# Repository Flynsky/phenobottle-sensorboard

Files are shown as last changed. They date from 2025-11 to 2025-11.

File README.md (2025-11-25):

# Phenobottle Sensorboard
Schematic
## Getting Startet
- Connect via USB or USART0 to access a internal console.
  A good, easy to use Tool for this is the Arduino IDE. 
- Send "?" to this console for help on the avaliable commands.

## Picture
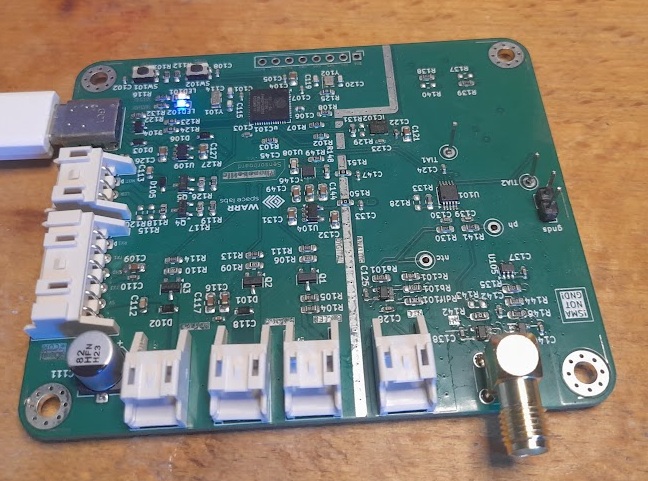
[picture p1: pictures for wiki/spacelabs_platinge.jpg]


## Hardware
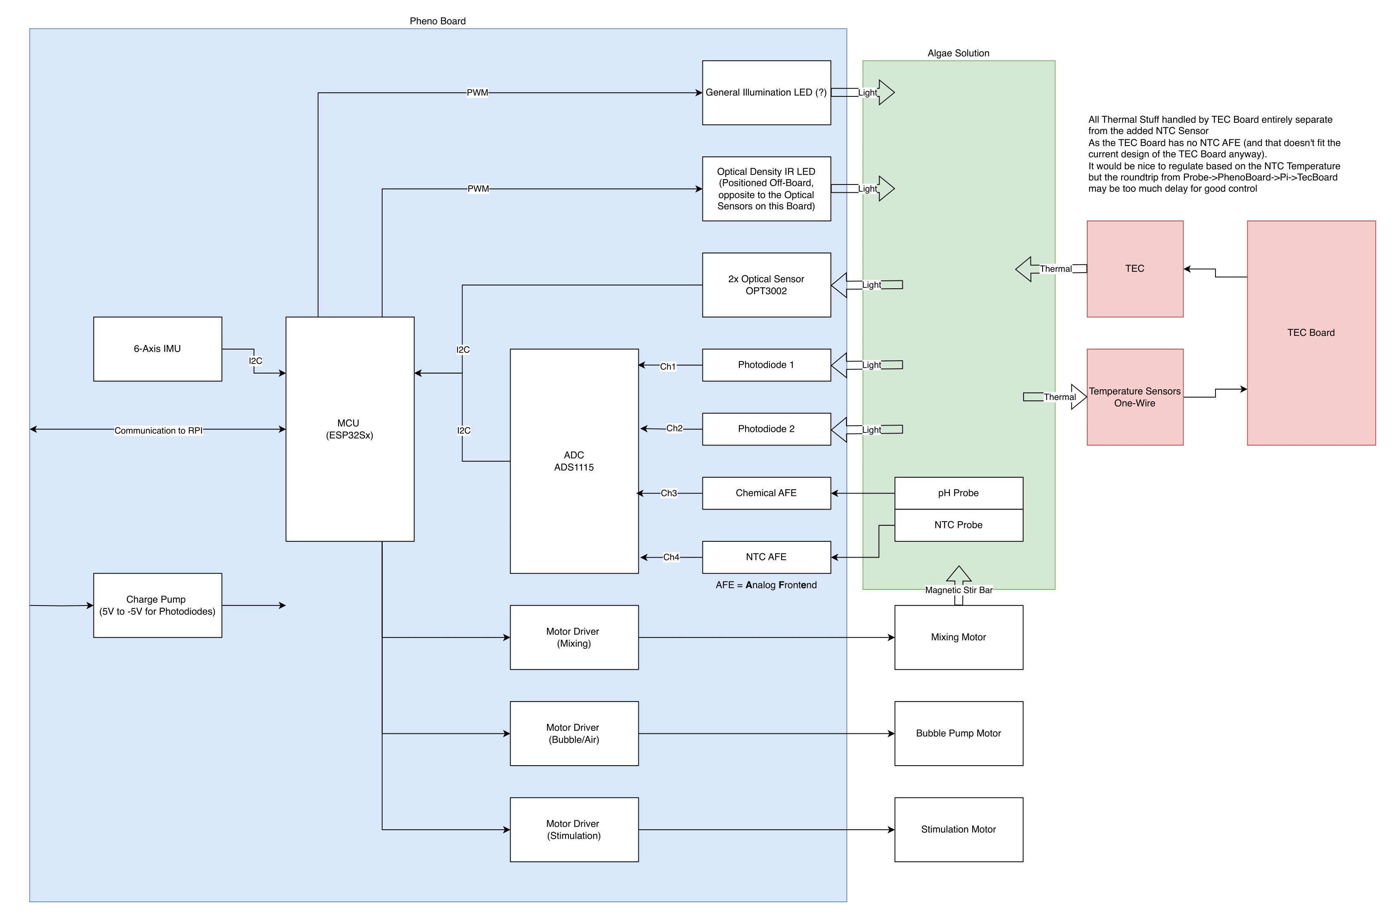
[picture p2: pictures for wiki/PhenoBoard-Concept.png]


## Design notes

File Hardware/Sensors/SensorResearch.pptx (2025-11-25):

## PyroSience (https://www.pyroscience.com/en/products/laboratory-solutions/oxygen-sensors)

Dissolved O2

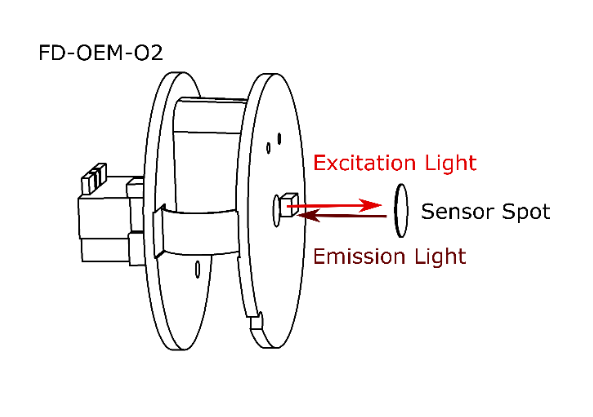
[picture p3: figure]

- If not sponsored 450€ a Sensor + 300€ for 6 spots + Extra Hardware required BUT they did sponsor 75% + gave some for free
- Not on the Website!
- Small Footprint
- Also measures ambient UV light, ambient pressure, ambient temperature & ambient humidity
- UART based. Software (in C) exisiting
- Maybe for free from SpiCy in February?
- Non intrusive
- Also available for PH & Temperature

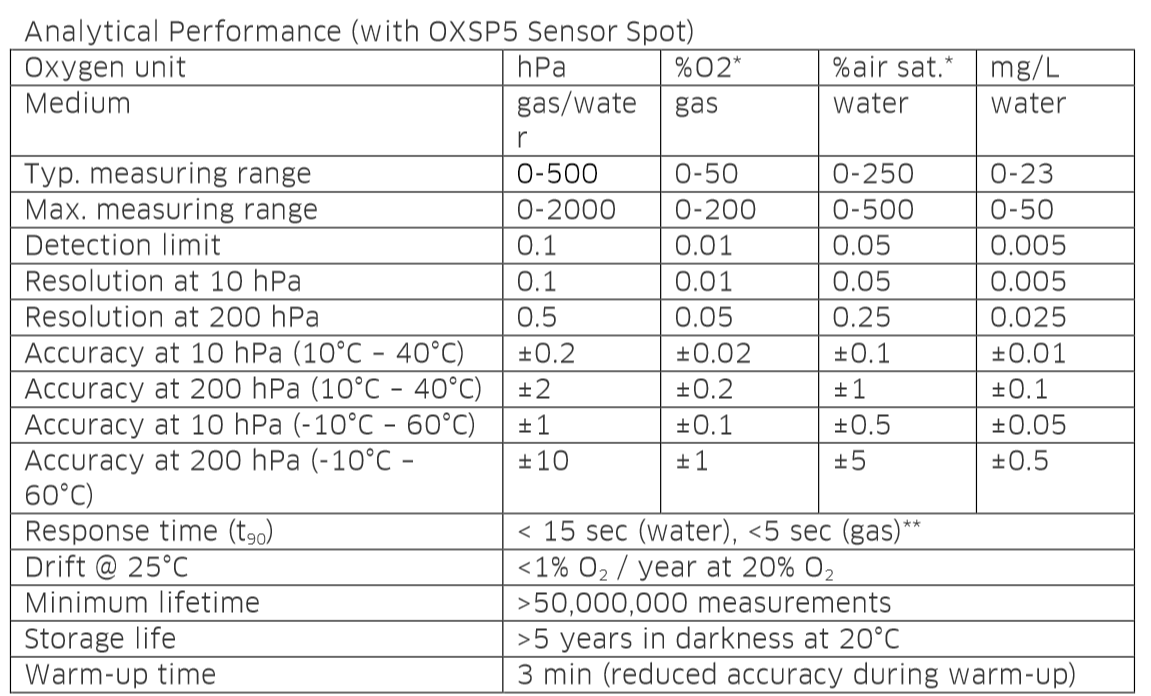
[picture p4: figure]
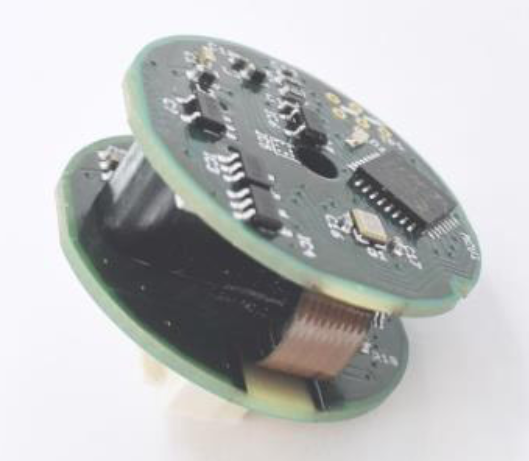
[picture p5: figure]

## AtlasScientific (https://atlas-scientific.com/kits/dissolved-oxygen-kit/)

Dissolved O2

- 354€ for full kit, probe 160€ I got one we can use
- Quite huge (12cm), made for pipes
- UART & I2C based. Very pleasant in terms of software
- Intrusive, uses up a bit of oxygen (60ml/min , https://files.atlas-scientific.com/DO_EZO_Datasheet.pdf page 70)
- Also available for PH (https://atlas-scientific.com/ph/)(175€ kit 40€ sensor) & Temperature

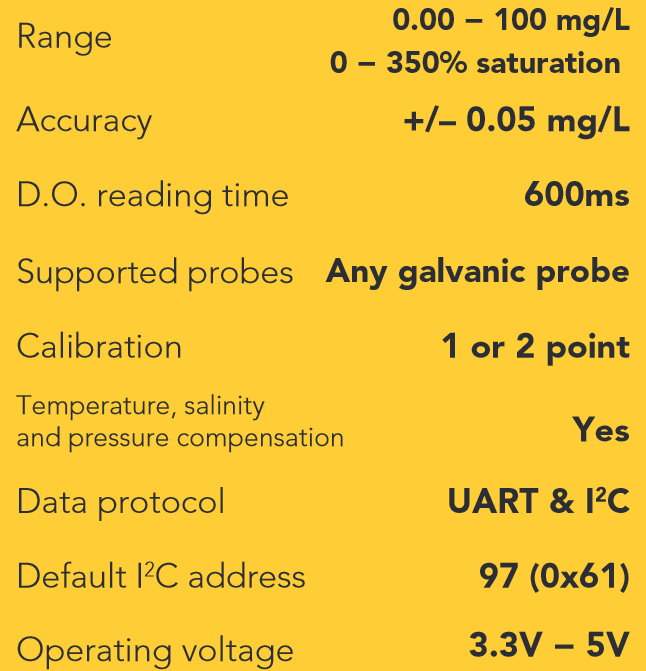
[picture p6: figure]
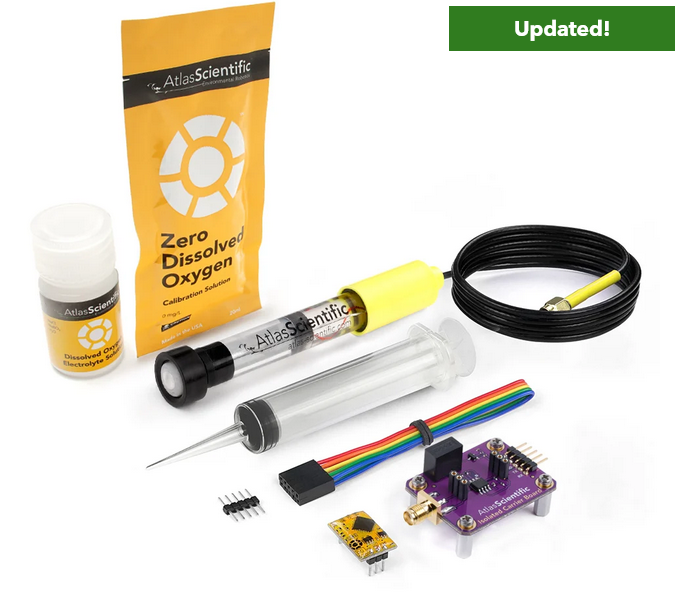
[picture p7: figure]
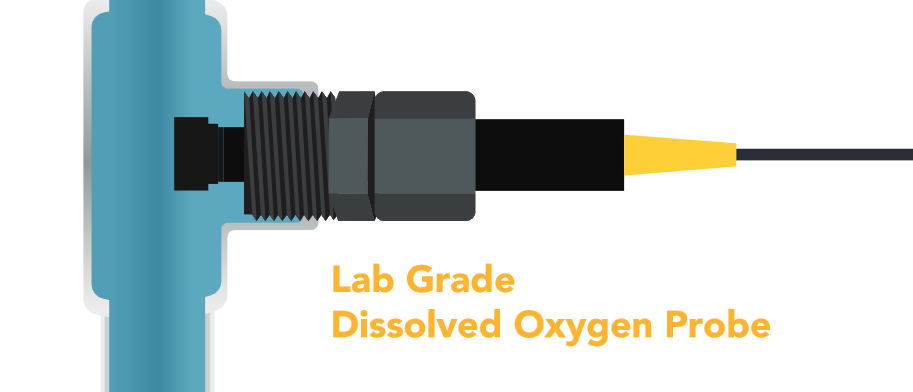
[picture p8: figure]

## Gravity (https://www.berrybase.de/dfrobot-gravity-analoger-ph-sensor-meter-kit-v2)

PH

- 47,80€
- Analog Signal
- https://wiki.dfrobot.com/Gravity__Analog_pH_Sensor_Meter_Kit_V2_SKU_SEN0161-V2
- There are better versions available
- https://www.dfrobot.com/blog-1138.htm (https://www.dfrobot.com/blog-1138.html)
- https://www.mouser.de/ProductDetail/DFRobot/SEN0169?qs=lqAf%2FiVYw9h7p9WXQvmXEQ%3D%3D&mgh=1&vip=1&srsltid=AfmBOopwmsmAfMMLqLApefzCYbJ93YjBi-50N7S2uCjpQjift9l-HvWDkNI (https://www.dfrobot.com/blog-1138.html)
- l (https://www.dfrobot.com/blog-1138.html)

0-14PH
0.1 PH accuracy, I think?

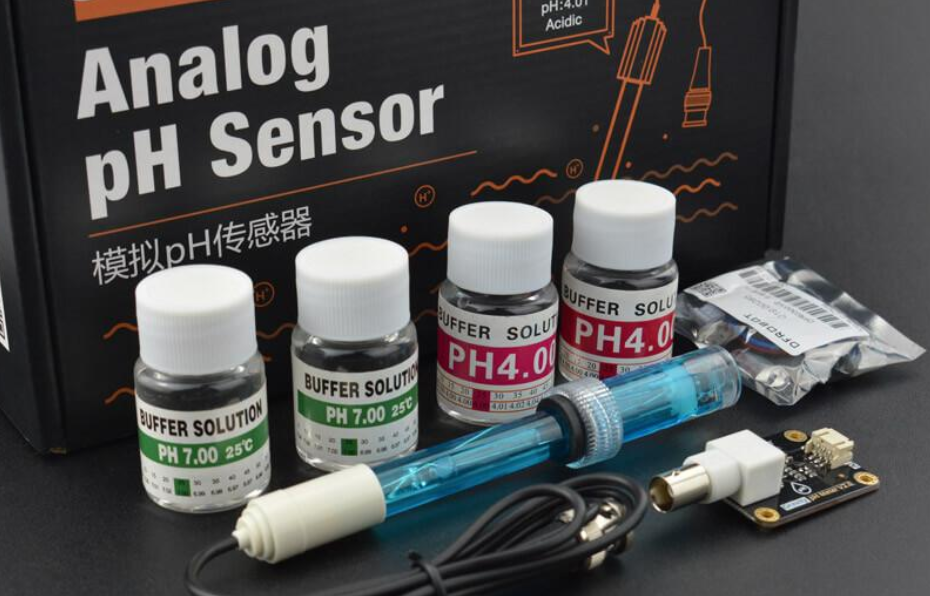
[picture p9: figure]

## Average Amazon Trash (https://www.amazon.de/Karosserie-Elektrode-Steckdose-0-14pH-Wirtschaftlich/dp/B07KG2PQMN)

PH

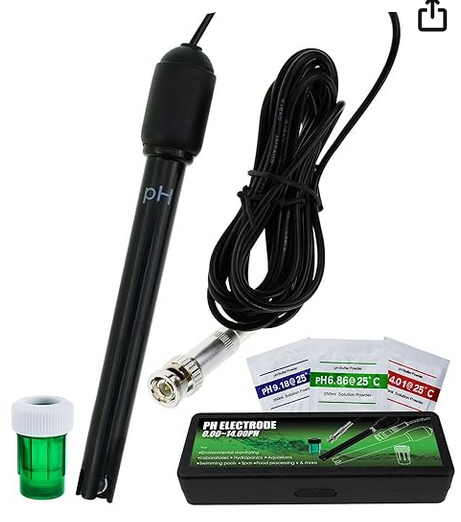
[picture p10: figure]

- 26,99€
- Analog Signal
- https://wiki.dfrobot.com/Gravity__Analog_pH_Sensor_Meter_Kit_V2_SKU_SEN0161-V2

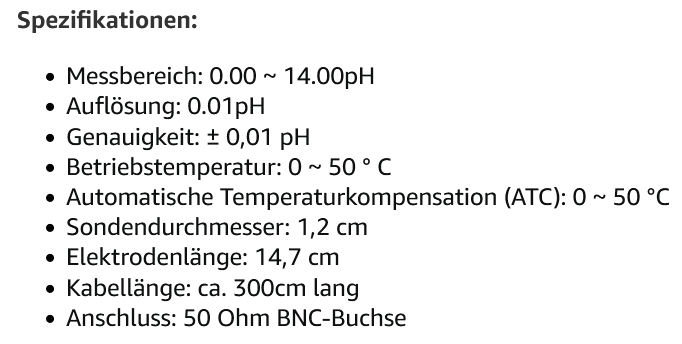
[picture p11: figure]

## Gravity (https://www.amazon.de/DFRobot-SEN0189-Gravity-Analog-Turbidity/dp/B075T3CVH6)

Turbidity / optical density Sensor

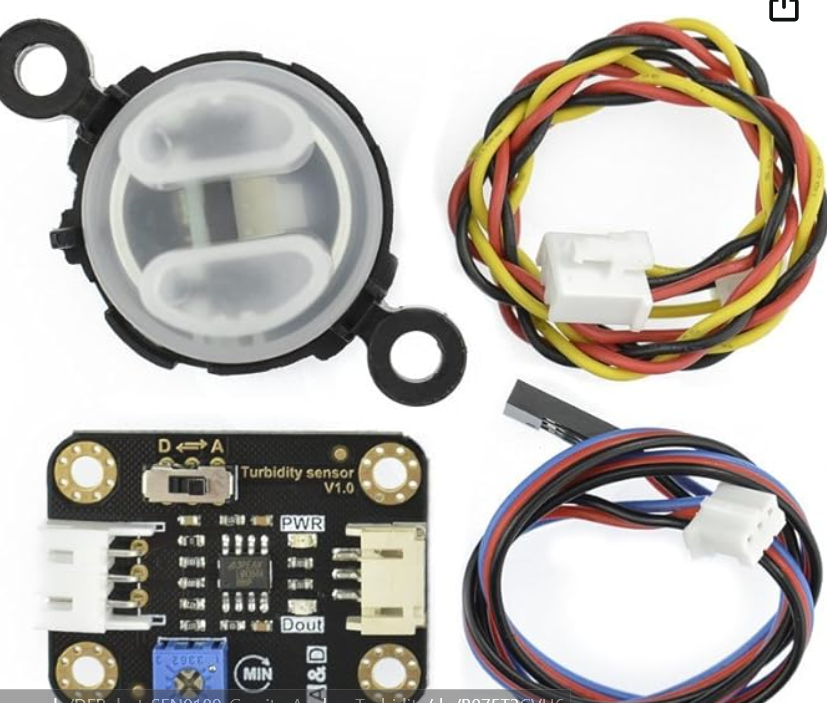
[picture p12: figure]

- 23€ amazon 8,3€ Farnell
- Analog Signal
- http://www.farnell.com/datasheets/2700162.pdf

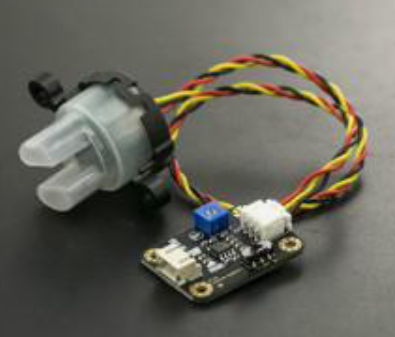
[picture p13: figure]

## AS7265x (https://www.sparkfun.com/products/15050)

Light spektrometer

- 69.95€ (~15€ per Sensor)
- Sparkfun light spektrometers
- can detect the light from 410nm (UV) to 940nm (IR)
- 18 individual light frequencies can be measured with precision down to 28.6 nW/cm2 and accuracy of +/-12%.

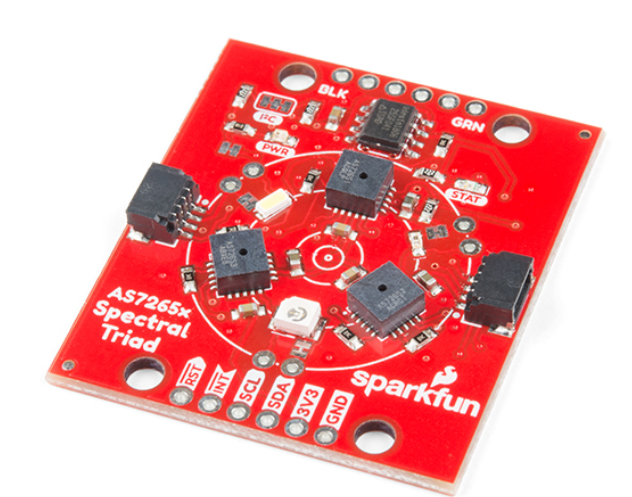
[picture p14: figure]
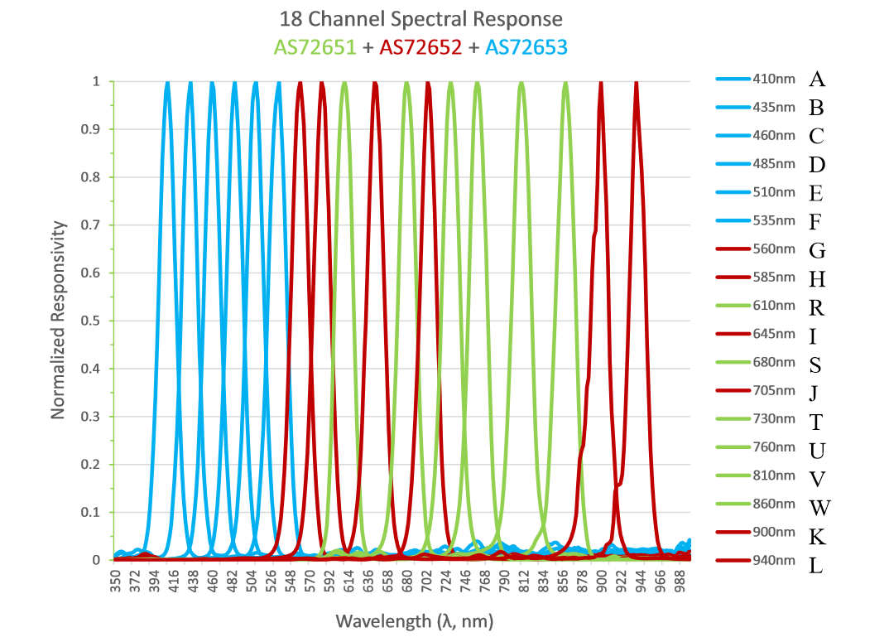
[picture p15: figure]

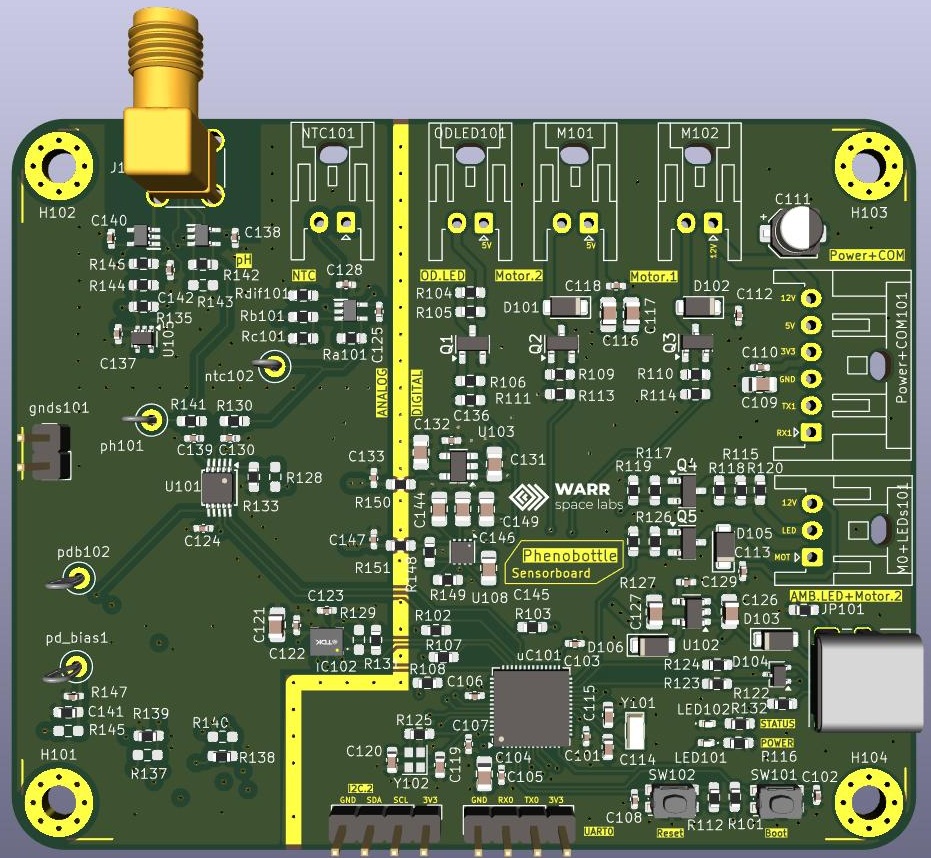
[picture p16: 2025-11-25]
pictures for wiki/render.jpg

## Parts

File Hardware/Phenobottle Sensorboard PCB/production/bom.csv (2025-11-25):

Designator | Footprint | Quantity | Value | LCSC Part #
C1, C2, C3 | 0603 | 3 | 1n
C101, C102, C103, C105, C106, C107, C108, C110, C118, C122, C123, C124, C125, C128, C130, C133, C134, C135, C137, C138, C139, C140, C142, C143, C147, C148 | 0402 | 26 | 100n
C104, C109, C116, C117, C121, C126, C127, C131, C132, C144, C146, C149 | 0805 | 12 | 10u
C111 | CP_Elec_6.3x7.7 | 1 | 45u
C112, C113, C151 | 0603 | 3 | 100n
C114, C115 | 0603 | 2 | 22p
C119, C120 | 0603 | 2 | 12p
C141, C150 | 0603 | 2 | 10n
C145 | 0805 | 1 | 1u
D101, D102, D103, D105, D106 | DIOM179X85N | 5 | CDBU0245-HF
D104 | SOT-323_SC-70 | 1 | ESD2CAN24DCKRQ1
D107, D108 | TEMD5080X01 | 2 | TEMD5080X01
GNDS1 | PinHeader_1x02_P2.54mm_Vertical | 1 | Conn_01x02_Pin
I2C1 | PinHeader_1x08_P2.54mm_Vertical | 1 | Conn_01x08_Pin
IC101, IC103, IC104 | SOT65P210X110-5N | 3 | OPA396DCKR
IC102 | ICM42670P | 1 | ICM-42670-P
J101 | USB_C_Receptacle_GCT_USB4085 | 1 | USB4085-GF-A
J102 | SMA_Wurth_60312002114503_Vertical | 1 | SMA
JP101, R123, R124, R125, R142, R150, R151 | 0603 | 7 | 0
LED101, LED102 | 0603 | 2 | LED_0603
M0, M1, NTC1, ODLED1 | JST_XA_S02B-XASK-1_1x02_P2.50mm_Horizontal | 4 | XA_S02B
M2+LEDS1 | JST_XA_S03B-XASK-1_1x03_P2.50mm_Horizontal | 1 | XA_S03B
POWER+COM1 | JST_XA_S06B-XASK-1_1x06_P2.50mm_Horizontal | 1 | XA_S06B
Q1, Q2, Q3, Q4, Q5 | SOT-23-3 | 5 | NTR4501NT1G
R1, R101, R112, R130, R141, R144, R146 | 0603 | 7 | 10k
R102, R103, R107, R108, R116, R132, R135 | 0603 | 7 | 2k2
R104, R105 | 0603 | 2 | 100/min 60mW
R106, R109, R110, R117, R126 | 0603 | 5 | 220
R111, R113, R114, R119, R127, R131, R133, R138, R139, R3 | 0603 | 10 | 100k
R115, R118, R120 | 0603 | 3 | 480
R121, R122, RA101, RB101 | 0603 | 4 | 5.1k
R148, RDIF101 | 0603 | 2 | 20k
R149 | 0603 | 1 | 50k
R2, R5 | 0603 | 2 | 1k
R4 | 0603 | 1 | 100
RC101 | 0603 | 1 | 40k
SW101, SW102 | SW_SPST_CK_KMS2xxGP | 2 | KMR223GLFG
TIA1, TIA2 | TestPoint_Loop_D2.50mm_Drill1.0mm | 2 | TestPoint_Small
U1 | VSSOP-8_SOP65P490X110-8N | 1 | OPA2328DGKR
U101 | TSSOP-10_3x3mm_P0.5mm | 1 | ADS1115IDGS
U104, U109 | SOT-23-5 | 2 | MIC5504-3.3YM5
U105 | SOT-353_SC-70-5 | 1 | LM4040DCK-2.0
U106, U107 | OPT3002DNPR | 2 | OPT3002DNPR
U108 | WSON-8-1EP_2x2mm_P0.5mm_EP0.9x1.6mm | 1 | LM27761
UC101 | QFN-56-1EP_7x7mm_P0.4mm_EP4x4mm | 1 | ESP32-S3
Y101 | Crystal_SMD_3215-2Pin_3.2x1.5mm | 1 | ECX-.327-CDX-1293
Y102 | Crystal_SMD_2016-4Pin_2.0x1.6mm | 1 | ECS-400-10-37B2-CKM-TR

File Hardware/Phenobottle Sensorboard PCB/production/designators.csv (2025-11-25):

C1:1
C101:1
C102:1
C103:1
C104:1
C105:1
C106:1
C107:1
C108:1
C109:1
C110:1
C111:1
C112:1
C113:1
C114:1
C115:1
C116:1
C117:1
C118:1
C119:1
C120:1
C121:1
C122:1
C123:1
C124:1
C125:1
C126:1
C127:1
C128:1
C130:1
C131:1
C132:1
C133:1
C134:1
C135:1
C137:1
C138:1
C139:1
C140:1
C141:1
C142:1
C143:1
C144:1
C145:1
C146:1
C147:1
C148:1
C149:1
C150:1
C151:1
C2:1
C3:1
D101:1
D102:1
D103:1
D104:1
D105:1
D106:1
D107:1
D108:1
G***:1
GNDS1:1
H101:1
H102:1
H103:1
H104:1
I2C1:1
IC101:1
IC102:1
IC103:1
IC104:1
J101:1
J102:1
JP101:1
LED101:1
LED102:1
M0:1
M1:1
M2+LEDS1:1
NTC1:1
NTC2:1
ODLED1:1
PH1:1
POWER+COM1:1
Q1:1
Q2:1
Q3:1
Q4:1
Q5:1
R1:1
R101:1
R102:1
R103:1
R104:1
R105:1
R106:1
R107:1
R108:1
R109:1
R110:1
R111:1
R112:1
R113:1
R114:1
R115:1
R116:1
R117:1
R118:1
R119:1
R120:1
R121:1
R122:1
R123:1
R124:1
R125:1
R126:1
R127:1
R128:1
R129:1
R130:1
R131:1
R132:1
R133:1
R135:1
R137:1
R138:1
R139:1
R140:1
R141:1
R142:1
R143:1
R144:1
R146:1
R148:1
R149:1
R150:1
R151:1
R2:1
R3:1
R4:1
R5:1
RA101:1
RB101:1
RC101:1
RDIF101:1
SW101:1
SW102:1
TIA1:1
TIA2:1
U1:1
U101:1
U104:1
U105:1
U106:1
U107:1
U108:1
U109:1
UC101:1
Y101:1
Y102:1

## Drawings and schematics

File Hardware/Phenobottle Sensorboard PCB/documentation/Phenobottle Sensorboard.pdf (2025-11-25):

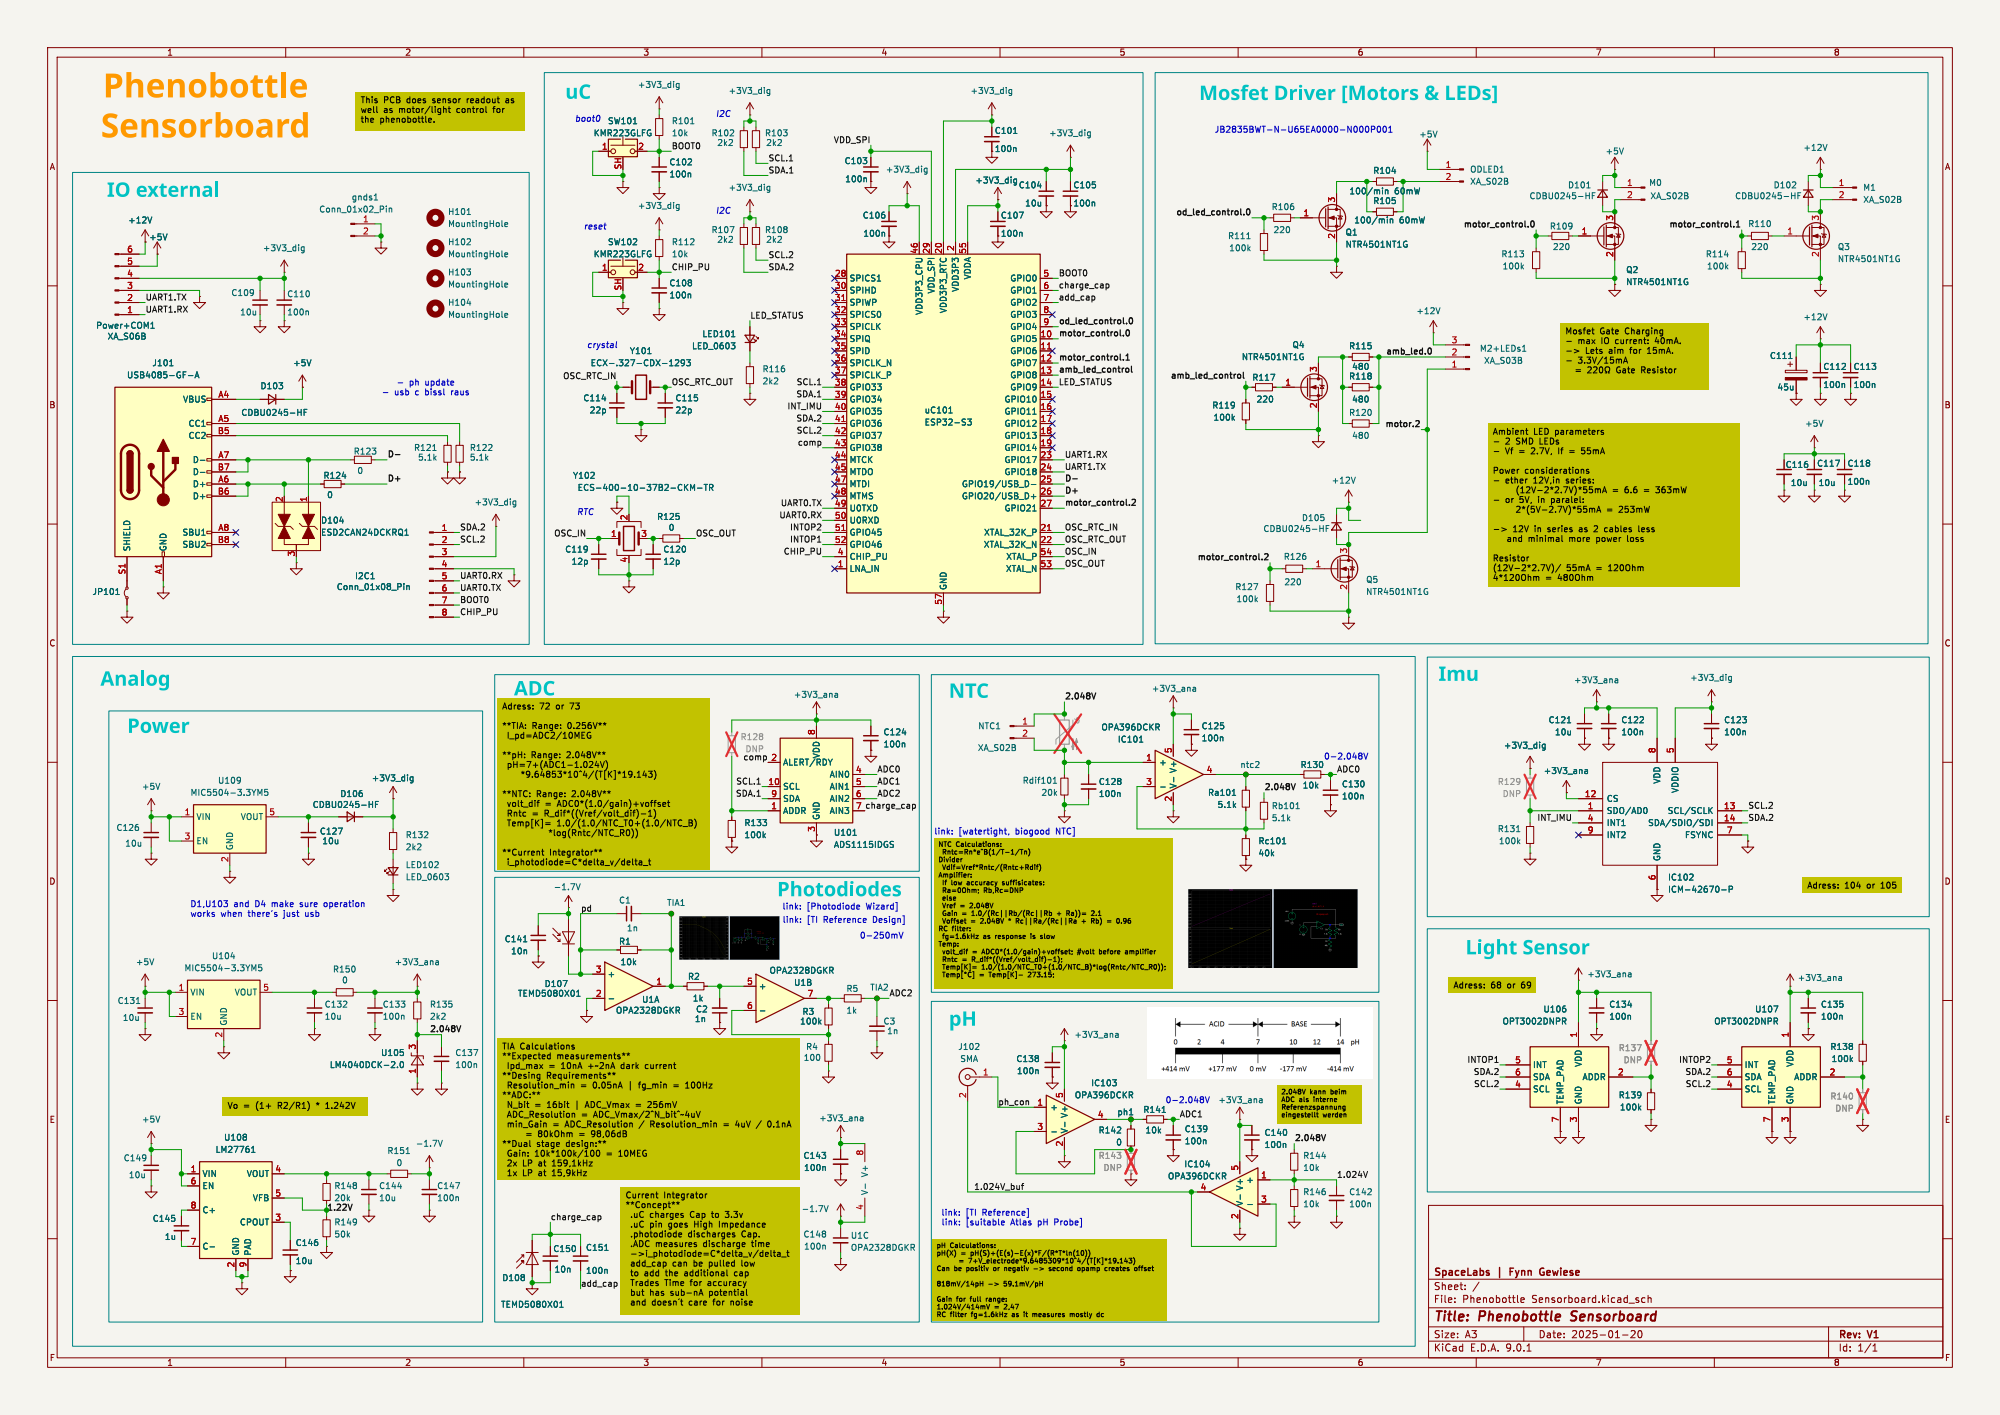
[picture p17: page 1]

Mosfet Driver [Motors & LEDs]

2 VDD3P3_RTC 20 GND 57 VDD_SPI 29 VDD3P3_CPU 46 SPICS1 28 SPIHD 30 SPIWP 31 SPICS0 32 SPICLK 33 SPIQ 34 SPID 35 SPICLK_P 37 GPIO33 38 GPIO34 39 GPIO35 40 GPIO36 41 GPIO37 42 GPIO38 43 MTCK 44 MTDI 47 MTMS 48 U0TXD 49 U0RXD 50 GPIO46 52 CHIP_PU 4

= þÿ220©Gate Resistor Ambient LED parameters

3 ALERT/RDY 2 SCL 10 SDA 9 ADDR 1 C2

3 ALERT/RDY 2 SCL 10 SDA 9 ADDR 1 U101 ADS1115IDGS R133

NTC Calculations: Rntc=Rn*e^B(1/T-1/Tn) Divider Vdif=Vref*Rntc/(Rntc+Rdif) Amplifier:

link: [TI Reference Design] (https://www.ti.com/lit/ug/tidu535/tidu535.pdf)

ADC als interne Referenzspannung

**Concept**
.uC charges Cap to 3.3v
.uC pin goes High Impedance
->i_photodiode=C*delta_v/delta_t
add_cap can be pulled low

Id: 1/1 Title: Phenobottle Sensorboard

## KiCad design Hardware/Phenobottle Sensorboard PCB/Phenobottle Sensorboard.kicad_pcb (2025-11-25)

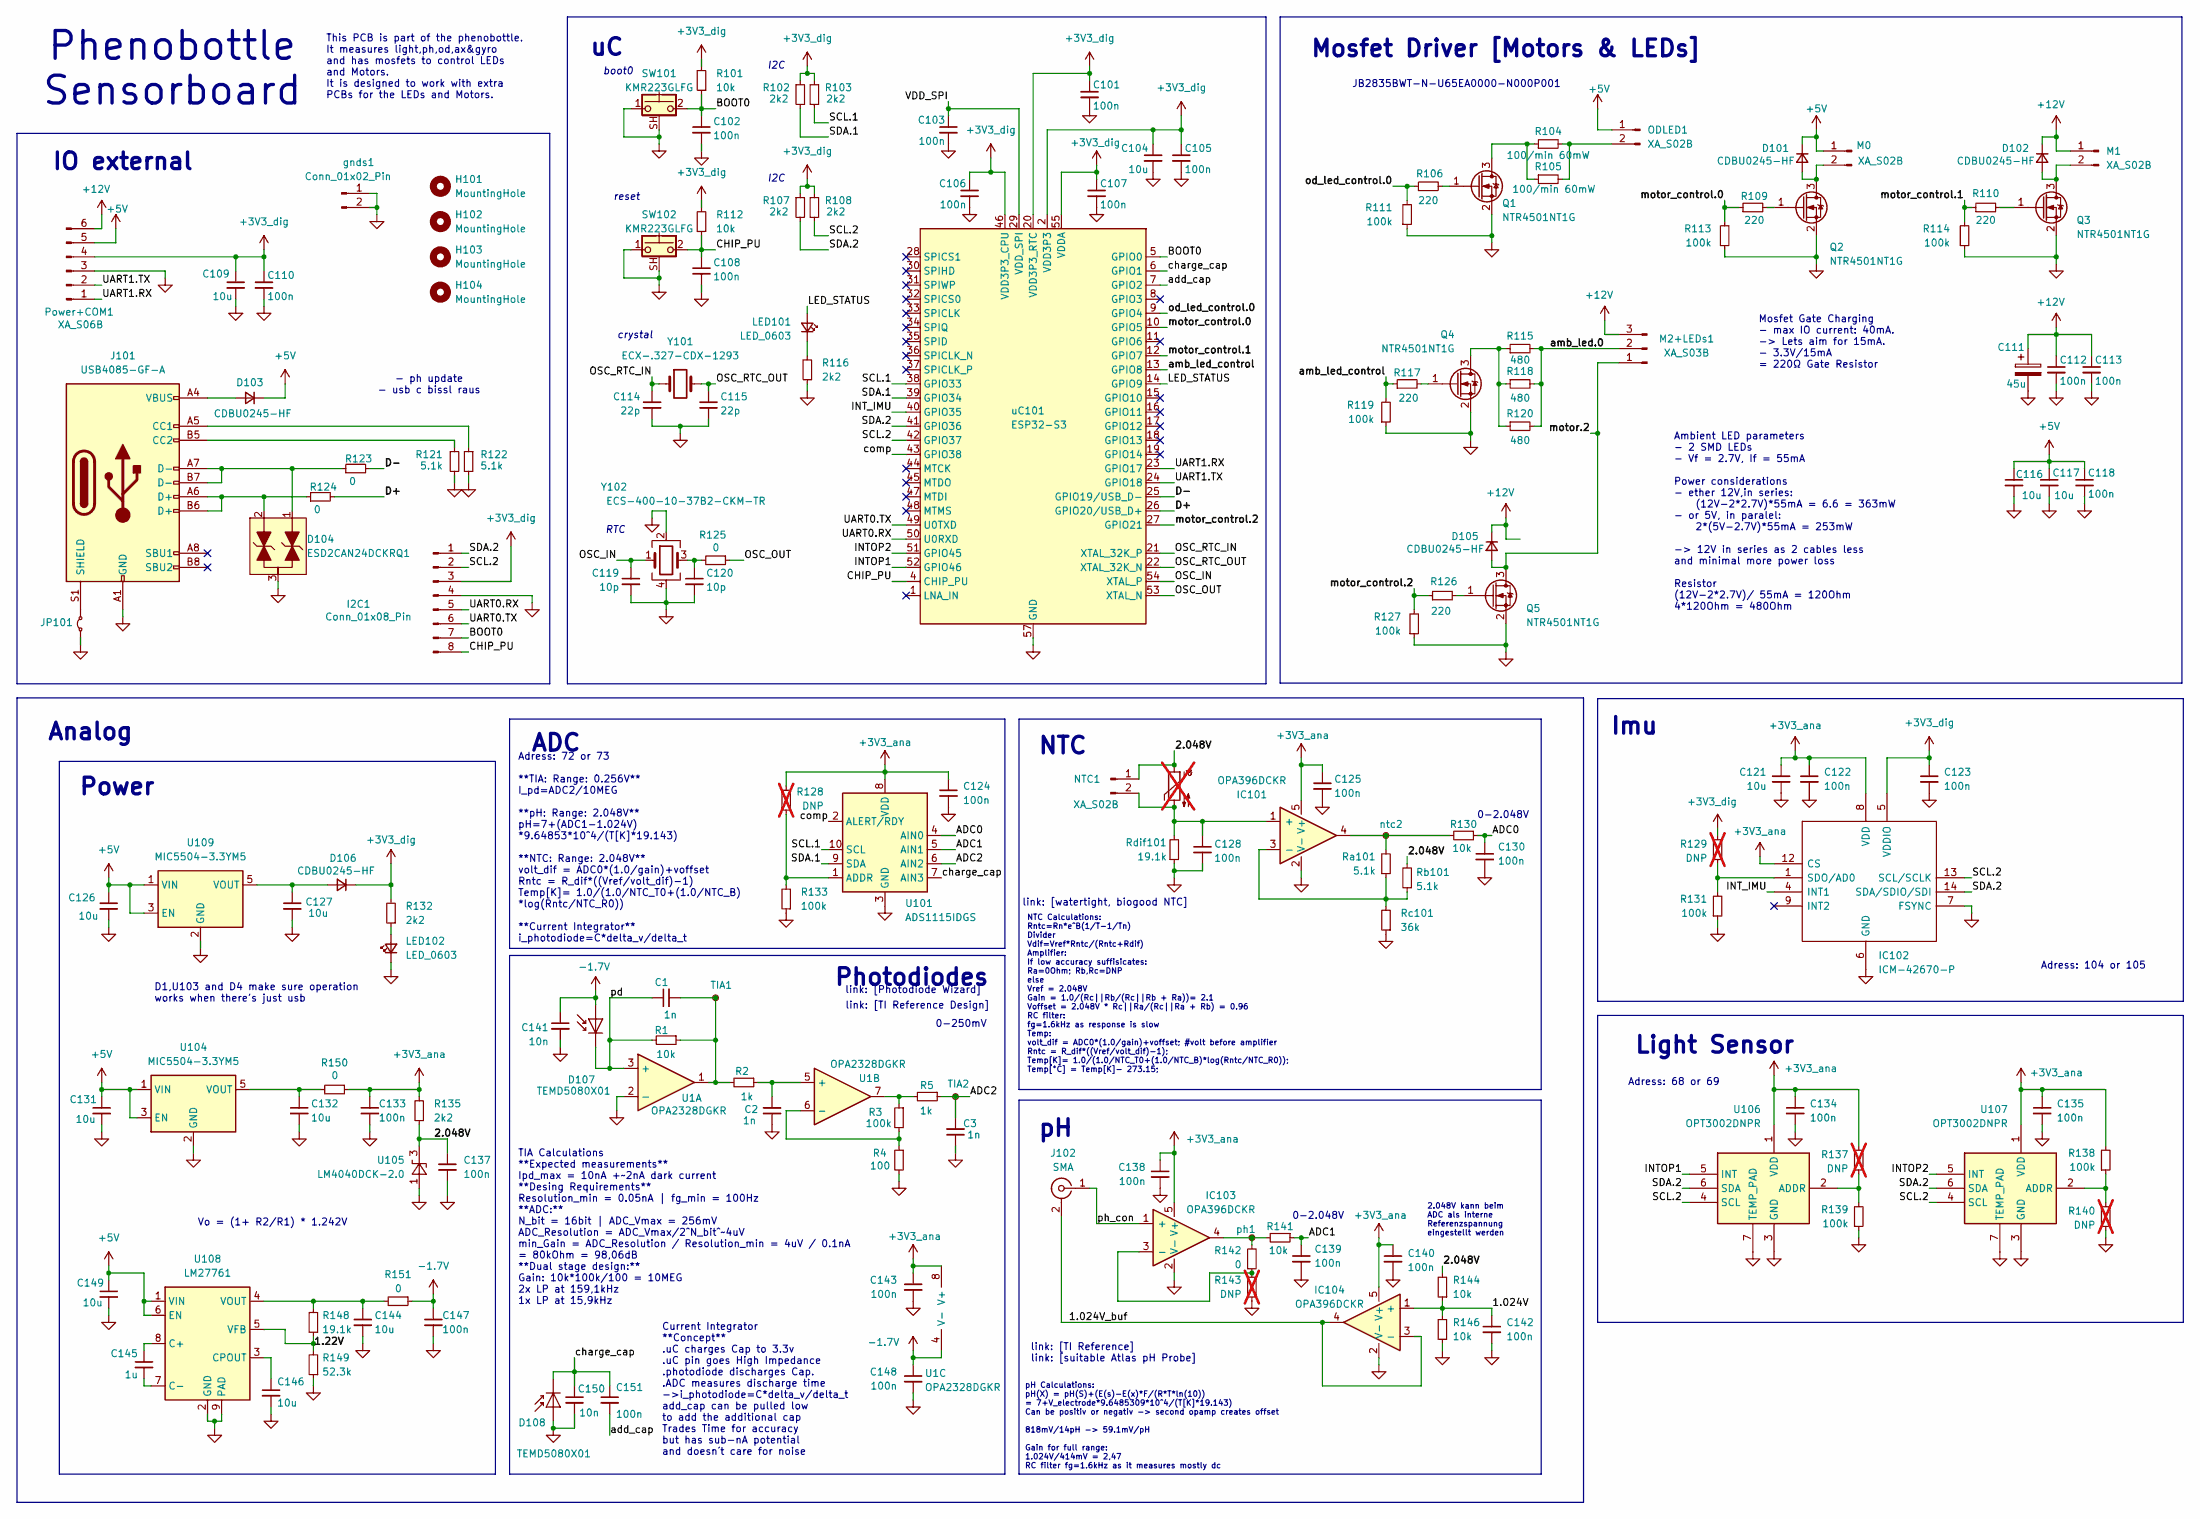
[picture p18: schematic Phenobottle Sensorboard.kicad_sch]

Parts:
C1, C2, C3: 1n; C_0603_1608Metric_Pad1.08x0.95mm_HandSolder
C101, C102, C103, C105, C106, C107, C108, C110, C118, C122, C123, C124, C125, C128, C130, C133, C134, C135, C137, C138, C139, C140, C142, C143, C147, C148: 100n; C_0402_1005Metric_Pad0.74x0.62mm_HandSolder
C104, C109, C116, C117, C121, C126, C127, C131, C132, C144, C146, C149: 10u; C_0805_2012Metric_Pad1.18x1.45mm_HandSolder
C111: 45u; CP_Elec_6.3x7.7
C112, C113, C151: 100n; C_0603_1608Metric
C114, C115: 22p; C_0603_1608Metric
C119, C120: 10p; C_0603_1608Metric
C141, C150: 10n; C_0603_1608Metric
C145: 1u; C_0805_2012Metric_Pad1.18x1.45mm_HandSolder
D101, D102, D103, D105, D106: CDBU0245-HF; DIOM179X85N; Mouser Part Number 78-V1FM15-M3/I; mouser 78-V1FM15-M3/I
D104: ESD2CAN24DCKRQ1; SOT-323_SC-70; Manufacturer_Part_Number ESD2CAN24DCKRQ1; Mouser Part Number 595-ESD2CAN24DCKRQ1
D107, D108: TEMD5080X01; Mouser Part Number 720-SFH2440
H101, H102, H103, H104: MountingHole; MountingHole_3.2mm_M3_Pad_Via
I2C1: Conn_01x08_Pin; PinHeader_1x08_P2.54mm_Vertical
IC101, IC103, IC104: OPA396DCKR; SOT65P210X110-5N; Mouser Part Number 595-OPA396DCKR
IC102: ICM-42670-P; ICM42670P; Mouser Part Number 410-ICM-42670-P
J101: USB4085-GF-A; USB_C_Receptacle_GCT_USB4085; Mouser Part Number 640-USB4085-GF-A
J102: SMA; SMA_Wurth_60312002114503_Vertical; Mouser Part Number 737-RF203ET0050G; mouser 471-SMARACONNECTOR
JP101: 0; R_0603_1608Metric_Pad0.98x0.95mm_HandSolder
LED101, LED102: LED_0603; LED_0603_1608Metric_Pad1.05x0.95mm_HandSolder
M0, M1: XA_S02B; JST_XA_S02B-XASK-1_1x02_P2.50mm_Horizontal
M2+LEDs1: XA_S03B; JST_XA_S03B-XASK-1_1x03_P2.50mm_Horizontal
NTC1: XA_S02B; JST_XA_S02B-XASK-1_1x02_P2.50mm_Horizontal
ODLED1: XA_S02B; JST_XA_S02B-XASK-1_1x02_P2.50mm_Horizontal
Power+COM1: XA_S06B; JST_XA_S06B-XASK-1_1x06_P2.50mm_Horizontal
Q1, Q2, Q3, Q4, Q5: NTR4501NT1G; SOT-23-3; Mouser Part Number 863-NTR4501NT1G
R1, R101, R112, R130, R141, R144, R146: 10k; R_0603_1608Metric_Pad0.98x0.95mm_HandSolder
R2, R5: 1k; R_0603_1608Metric_Pad0.98x0.95mm_HandSolder
R3, R111, R113, R114, R119, R127, R131, R133, R138, R139: 100k; R_0603_1608Metric_Pad0.98x0.95mm_HandSolder
R4: 100; R_0603_1608Metric_Pad0.98x0.95mm_HandSolder
R102, R103, R107, R108, R116, R132, R135: 2k2; R_0603_1608Metric_Pad0.98x0.95mm_HandSolder
R104, R105: 100/min 60mW; R_0603_1608Metric_Pad0.98x0.95mm_HandSolder
R106, R109, R110, R117, R126: 220; R_0603_1608Metric_Pad0.98x0.95mm_HandSolder
R115, R118, R120: 480; R_0603_1608Metric_Pad0.98x0.95mm_HandSolder
R121, R122: 5.1k; R_0603_1608Metric_Pad0.98x0.95mm_HandSolder
R123, R124, R125, R142, R150, R151: 0; R_0603_1608Metric_Pad0.98x0.95mm_HandSolder
R128, R129, R137, R140, R143: DNP; R_0603_1608Metric_Pad0.98x0.95mm_HandSolder; not fitted
R148: 19.1k; R_0603_1608Metric_Pad0.98x0.95mm_HandSolder
R149: 52.3k; R_0603_1608Metric_Pad0.98x0.95mm_HandSolder
Ra101: 5.1k; R_0603_1608Metric_Pad0.98x0.95mm_HandSolder
Rb101: 5.1k; R_0603_1608Metric_Pad0.98x0.95mm_HandSolder
Rc101: 36k; R_0603_1608Metric_Pad0.98x0.95mm_HandSolder
Rdif101: 19.1k; R_0603_1608Metric_Pad0.98x0.95mm_HandSolder
SW101, SW102: KMR223GLFG; SW_SPST_CK_KMS2xxGP; Mouser Part Number 611-KMR223GLFG
TH101: Thermistor_NTC; mouser 527-JI-103C1R2-L301; not fitted
TIA1, TIA2: TestPoint_Small; TestPoint_Loop_D2.50mm_Drill1.0mm
U1: OPA2328DGKR; VSSOP-8_SOP65P490X110-8N; Mouser Part Number 595-OPT3002DNPR; mouser 595-OPA2328DGKR
U101: ADS1115IDGS; TSSOP-10_3x3mm_P0.5mm; Mouser Part Number 595-ADS1115IDGSR
U104, U109: MIC5504-3.3YM5; SOT-23-5
U105: LM4040DCK-2.0; SOT-353_SC-70-5; Mouser Part Number 595-M4040EIM7-2.0NPB
U106, U107: OPT3002DNPR; Mouser Part Number 595-OPT3002DNPR
U108: LM27761; WSON-8-1EP_2x2mm_P0.5mm_EP0.9x1.6mm; Mouser Part Number 595-LM27761DSGR
Y101: ECX-.327-CDX-1293; Crystal_SMD_3215-2Pin_3.2x1.5mm; Mouser Part Number 520-ECX-.327CDX-1293
Y102: ECS-400-10-37B2-CKM-TR; Crystal_SMD_2016-4Pin_2.0x1.6mm; Mouser Part Number 520-400-10-37B2CKMTR
gnds1: Conn_01x02_Pin; PinHeader_1x02_P2.54mm_Vertical
ntc2: TestPoint_Small; TestPoint_Loop_D2.50mm_Drill1.0mm
ph1: TestPoint_Small; TestPoint_Loop_D2.50mm_Drill1.0mm
uC101: ESP32-S3; QFN-56-1EP_7x7mm_P0.4mm_EP4x4mm; Mouser Part Number 356-ESP32-S3FH4R2

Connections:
+3V3_ana: C121.1, C122.1, C124.1, C125.1, C133.1, C134.1, C135.1, C138.1, C140.1, C143.1, IC101.5 (V+), IC102.8 (VDD), IC102.12 (CS), IC103.5 (V+), IC104.5 (V+), R128.2, R135.2, R137.1, R138.2, R150.1, U1.8 (V+), U101.8 (VDD), U106.1 (VDD), U107.1 (VDD)
+3V3_dig: C101.1, C104.1, C105.1, C106.1, C107.1, C109.1, C110.1, C123.1, D106.1 (K), I2C1.3, IC102.5 (VDDIO), Power+COM1.4, R101.2, R102.1, R103.1, R107.1, R108.1, R112.2, R129.1, R132.2, uC101.2 (VDD3P3), uC101.3 (VDD3P3), uC101.20 (VDD3P3_RTC), uC101.46 (VDD3P3_CPU), uC101.55 (VDDA), uC101.56 (VDDA)
+5V: C116.1, C117.1, C118.1, C126.1, C131.1, C149.1, D101.1 (K), D103.1 (K), M0.1, ODLED1.1, Power+COM1.5, U104.1 (VIN), U104.3 (EN), U108.1 (VIN), U108.6 (EN), U109.1 (VIN), U109.3 (EN)
+12V: C111.1, C112.1, C113.1, D102.1 (K), D105.1 (K), M1.1, M2+LEDs1.3, Power+COM1.6
-1.7V: C141.1, C147.1, C148.1, D107.2 (A), R151.1, U1.4 (V-)
/1.22V: R148.1, R149.2, U108.5 (VFB)
/1.024V: C142.1, IC104.1 (+), R144.1, R146.2
/1.024V_buf: IC104.3 (-), IC104.4, J102.2 (Ext)
/2.048V: C137.1, NTC1.1, R135.1, R144.2, Rb101.2, TH101.1, U105.3 (K)
/ADC0: C130.1, R130.1, U101.4 (AIN0)
/ADC1: C139.1, R141.1, U101.5 (AIN1)
/ADC2: C3.2, R5.1, TIA2.1, U101.6 (AIN2)
/BOOT0: C102.1, I2C1.7, R101.1, SW101.2, uC101.5 (GPIO0)
/CHIP_PU: C108.1, I2C1.8, R112.1, SW102.2, uC101.4 (CHIP_PU)
/D+: R124.2, uC101.26 (GPIO20/USB_D+)
/D-: R123.2, uC101.25 (GPIO19/USB_D-)
/INTOP1: U106.5 (INT), uC101.52 (GPIO46)
/INTOP2: U107.5 (INT), uC101.51 (GPIO45)
/INT_IMU: IC102.4 (INT1), uC101.40 (GPIO35)
/LED_STATUS: LED101.2 (A), uC101.14 (GPIO9)
/OSC_IN: C119.1, Y102.1, uC101.54 (XTAL_P)
/OSC_OUT: R125.1, uC101.53 (XTAL_N)
/OSC_RTC_IN: C114.1, Y101.1, uC101.21 (XTAL_32K_P)
/OSC_RTC_OUT: C115.1, Y101.2, uC101.22 (XTAL_32K_N)
/SCL.1: R103.2, U101.10 (SCL), uC101.38 (GPIO33)
/SCL.2: I2C1.2, IC102.13 (SCL/SCLK), R108.2, U106.4 (SCL), U107.4 (SCL), uC101.42 (GPIO37)
/SDA.1: R102.2, U101.9 (SDA), uC101.39 (GPIO34)
/SDA.2: I2C1.1, IC102.14 (SDA/SDIO/SDI), R107.2, U106.6 (SDA), U107.6 (SDA), uC101.41 (GPIO36)
/UART0.RX: I2C1.5, uC101.50 (U0RXD)
/UART0.TX: I2C1.6, uC101.49 (U0TXD)
/UART1.RX: Power+COM1.1, uC101.23 (GPIO17)
/UART1.TX: Power+COM1.2, uC101.24 (GPIO18)
/VDD_SPI: C103.1, uC101.29 (VDD_SPI)
/add_cap: C151.2, uC101.7 (GPIO2)
/amb_led.0: M2+LEDs1.2, R115.2, R118.2, R120.2
/amb_led_control: R117.1, R119.2, uC101.13 (GPIO8)
/charge_cap: C150.1, C151.1, D108.1 (K), U101.7 (AIN3), uC101.6 (GPIO1)
/comp: U101.2 (ALERT/RDY), uC101.43 (GPIO38)
/motor.2: D105.2 (A), M2+LEDs1.1, Q5.3 (D)
/motor_control.0: R109.1, R113.2, uC101.10 (GPIO5)
/motor_control.1: R110.1, R114.2, uC101.12 (GPIO7)
/motor_control.2: R126.1, R127.2, uC101.27 (GPIO21)
/od_led_control.0: R106.1, R111.2, uC101.9 (GPIO4)
/pd: C1.1, D107.1 (K), R1.2, U1.3 (+)
/ph_con: IC103.1 (+), J102.1 (In)
GND: C2.1, C3.1, C101.2, C102.2, C103.2, C104.2, C105.2, C106.2, C107.2, C108.2, C109.2, C110.2, C111.2, C112.2, C113.2, C114.2, C115.2, C116.2, C117.2, C118.2, C119.2, C120.2, C121.2, C122.2, C123.2, C124.2, C125.2, C126.2, C127.2, C128.2, C130.2, C131.2, C132.2, C133.2, C134.2, C135.2, C137.2, C138.2, C139.2, C140.2, C141.2, C142.2, C143.2, C144.2, C146.2, C147.2, C148.2, C149.2, C150.2, D104.3, D108.2 (A), I2C1.4, IC101.2 (V-), IC102.6 (GND), IC102.7 (FSYNC), IC103.2 (V-), IC104.2 (V-), J101.A1 (GND), J101.A12 (GND), J101.B1 (GND), J101.B12 (GND), JP101.1 (A), LED102.1 (K), Power+COM1.3, Q1.2 (S), Q2.2 (S), Q3.2 (S), Q4.2 (S), Q5.2 (S), R4.2, R111.1, R113.1, R114.1, R116.1, R119.1, R121.2, R122.2, R127.1, R131.1, R133.1, R139.1, R140.2, R143.1, R146.1, R149.1, Rc101.1, Rdif101.1, SW101.1, SW101.SH (B), SW102.1, SW102.SH (B), U1.2 (-), U101.3 (GND), U104.2 (GND), U105.1 (A), U106.3 (GND), U106.7 (TEMP_PAD), U107.3 (GND), U107.7 (TEMP_PAD), U108.2 (GND), U108.9 (PAD), U109.2 (GND), Y102.2, Y102.4, gnds1.1, gnds1.2, uC101.57 (GND)
unnamed: C1.2, R1.1, R2.2, TIA1.1, U1.1
unnamed: C120.1, R125.2, Y102.3
unnamed: D101.2 (A), M0.2, Q2.3 (D)
unnamed: D102.2 (A), M1.2, Q3.3 (D)
unnamed: D103.2 (A), J101.A4 (VBUS), J101.A9 (VBUS), J101.B4 (VBUS), J101.B9 (VBUS)
unnamed: D104.1, J101.A7 (D-), J101.B7 (D-), R123.1
unnamed: D104.2, J101.A6 (D+), J101.B6 (D+), R124.1
unnamed: C127.1, D106.2 (A), U109.5 (VOUT)
unnamed: C128.1, IC101.1 (+), NTC1.2, Rdif101.2, TH101.2
unnamed: IC101.3 (-), Ra101.1, Rb101.1, Rc101.2
unnamed: IC101.4, R130.2, Ra101.2, ntc2.1
unnamed: IC102.1 (SDO/AD0), R129.2, R131.2
unnamed: IC103.3 (-), R142.1, R143.2
unnamed: IC103.4, R141.2, R142.2, ph1.1
unnamed: J101.A5 (CC1), R122.1
unnamed: J101.B5 (CC2), R121.1
unnamed: J101.S1 (SHIELD), JP101.2 (B)
unnamed: LED101.1 (K), R116.2
unnamed: LED102.2 (A), R132.1
unnamed: ODLED1.2, R104.2, R105.2
unnamed: Q1.3 (D), R104.1, R105.1
unnamed: Q1.1 (G), R106.2
unnamed: Q2.1 (G), R109.2
unnamed: Q3.1 (G), R110.2
unnamed: Q4.3 (D), R115.1, R118.1, R120.1
unnamed: Q4.1 (G), R117.2
unnamed: Q5.1 (G), R126.2
unnamed: R3.1, R5.2, U1.7
unnamed: C2.2, R2.1, U1.5 (+)
unnamed: R3.2, R4.1, U1.6 (-)
unnamed: R128.1, R133.2, U101.1 (ADDR)
unnamed: C132.1, R150.2, U104.5 (VOUT)
unnamed: R137.2, R139.2, U106.2 (ADDR)
unnamed: R138.1, R140.1, U107.2 (ADDR)
unnamed: C145.1, U108.8 (C+)
unnamed: C145.2, U108.7 (C-)
unnamed: C146.1, U108.3 (CPOUT)
unnamed: C144.1, R148.2, R151.2, U108.4 (VOUT)

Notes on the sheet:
Analog
Phenobottle Sensorboard
link: [TI Reference]
reset
boot0
I2C
link: [suitable Atlas pH Probe]
link: [watertight, biogood NTC]
ADC
crystal
Mosfet Driver [Motors & LEDs]
- ph update - usb c bissl raus
Light Sensor
IO external
link: [TI Reference Design]
0-250mV
0-2.048V
Photodiodes
link: [Photodiode Wizard]
Imu
Power
D1,U103 and D4 make sure operation works when there's just usb
NTC
JB2835BWT-N-U65EA0000-N000P001
RTC
Adress: 72 or 73 **TIA: Range: 0.256V** I_pd=ADC2/10MEG **pH: Range: 2.048V** pH=7+(ADC1-1.024V) *9.64853*10^4/(T[K]*19.143) **NTC: Range: 2.048V** volt_dif = ADC0*(1.0/gain)+voffset Rntc = R_dif*((Vref/volt_dif)-1) Temp[K]= 1.0/(1.0/NTC_T0+(1.0/NTC_B) *log(Rntc/NTC_R0)) **Current Integrator** i_ph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
2.048V kann beim ADC als interne Referenzspannung eingestellt werden
Current Integrator **Concept** .uC charges Cap to 3.3v .uC pin goes High Impedance .photodiode discharges Cap. .ADC measures discharge time ->i_photodiode=C*delta_v/delta_t add_cap can be pulled low to add the additional cap Trades Time for accuracy but has sub-nA potential and doesn´t care for noi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
Mosfet Gate Charging - max IO current: 40mA. -> Lets aim for 15mA. - 3.3V/15mA = 220Ω Gate Resistor
This PCB is part of the phenobottle. It measures light,ph,od,ax&gyro and has mosfets to control LEDs and Motors. It is designed to work with extra PCBs for the LEDs and Motors.
Adress: 104 or 105
pH Calculations: pH(X) = pH(S)+(E(s)-E(x)*F/(R*T*ln(10)) = 7+V_electrode*9.6485309*10^4/(T[K]*19.143) Can be positiv or negativ -> second opamp creates offset 818mV/14pH -> 59.1mV/pH Gain for full range: 1.024V/414mV = 2,47 RC filter fg=1.6kHz as it measures mostly dc
NTC Calculations: Rntc=Rn*e^B(1/T-1/Tn) Divider Vdif=Vref*Rntc/(Rntc+Rdif) Amplifier: If low accuracy suffisicates: Ra=0Ohm; Rb,Rc=DNP else Vref = 2.048V Gain = 1.0/(Rc||Rb/(Rc||Rb + Ra))= 2.1 Voffset = 2.048V * Rc||Ra/(Rc||Ra + Rb) = 0.96 RC filter: fg=1.6kHz as response is slow Temp: volt_dif = A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
Adress: 68 or 69
Ambient LED parameters - 2 SMD LEDs - Vf = 2.7V, If = 55mA Power considerations - ether 12V,in series: (12V-2*2.7V)*55mA = 6.6 = 363mW - or 5V, in paralel: 2*(5V-2.7V)*55mA = 253mW -> 12V in series as 2 cables less and minimal more power loss Resistor (12V-2*2.7V)/ 55mA = 120Ohm 4*120Ohm = 480Ohm
Vo = (1+ R2/R1) * 1.242V
TIA Calculations **Expected measurements** Ipd_max = 10nA +~2nA dark current **Desing Requirements** Resolution_min = 0.05nA | fg_min = 100Hz **ADC:** N_bit = 16bit | ADC_Vmax = 256mV ADC_Resolution = ADC_Vmax/2^N_bit^~4uV min_Gain = ADC_Resolution / Resolution_min = 4uV / 0.1nA = 80kOhm = 98,06dB 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

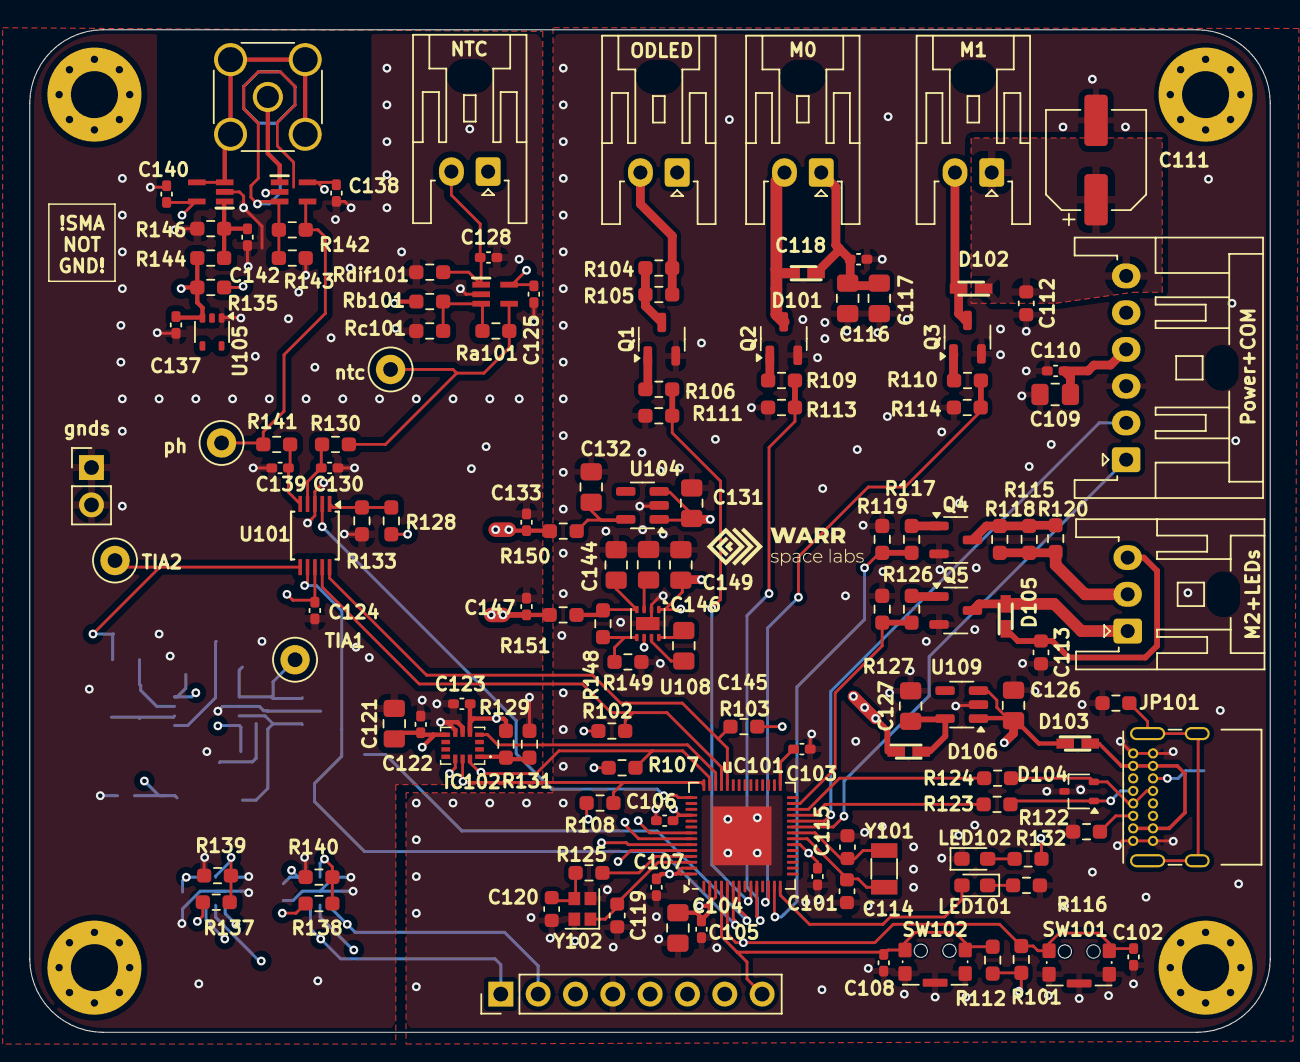
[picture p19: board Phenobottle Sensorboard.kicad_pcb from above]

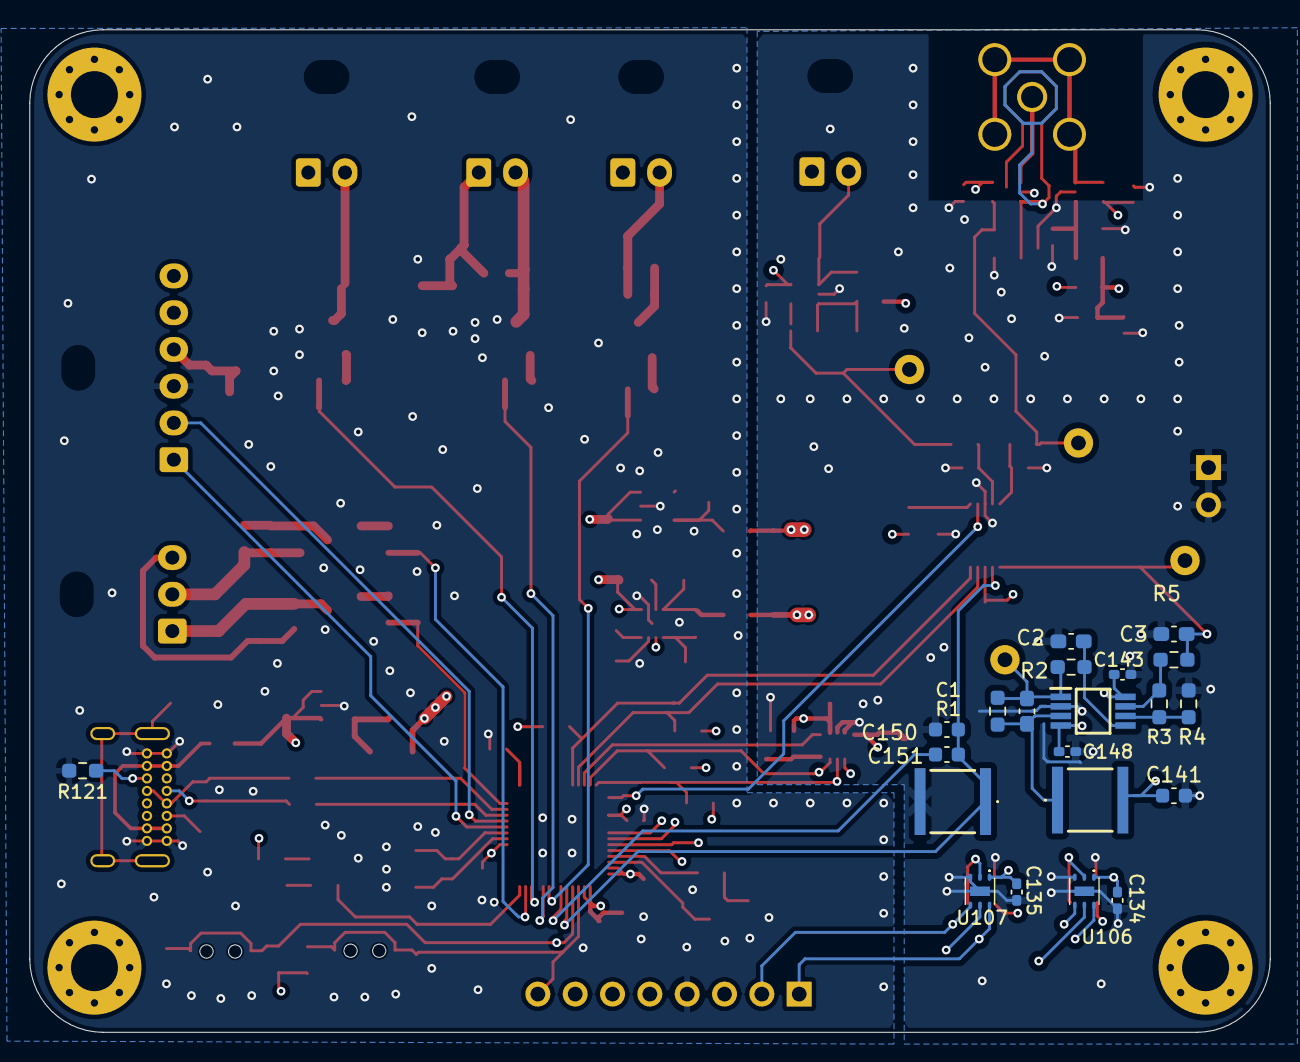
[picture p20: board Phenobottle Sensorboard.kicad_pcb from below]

Board: 4 copper layers, 84.4 x 68.2 mm, 159 parts (21 on the bottom side), 84 nets.

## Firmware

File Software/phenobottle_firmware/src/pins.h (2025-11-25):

#pragma once

typedef enum {
  PIN_LED_STATUS = 9,
  PIN_I2C1_SDA = 34, // ADC
  PIN_I2C1_SCL = 33, // ADC
  PIN_I2C2_SDA = 36, // IMU
  PIN_I2C2_SCL = 37, // IMU
  PIN_AMBIENT_LED = 8,
  PIN_OD_LED = 4,
  PIN_MOTOR0 = 5,
  PIN_MOTOR1 = 7,
  PIN_MOTOR2 = 21,
  PIN_INTEGRATOR_COMP = 38,
  PIN_INTEGRATOR_CHARGE_CAP = 1,
  PIN_INTEGRATOR_ADD_CAP = 2,
  PIN_OPT_INT_1 = 46, // left to shortest board edge
  PIN_OPT_INT_2 = 45,
} PIN_MAPPING;

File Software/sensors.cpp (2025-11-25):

// https://eu.mouser.com/ProductDetail/TDK/NTCGS163JF103FT8?qs=dbcCsuKDzFU4pk95bZlq7w%3D%3D&countryCode=DE&currencyCode=EUR
// https://www.mouser.de/ProductDetail/Amphenol-Advanced-Sensors/JI-103C1R2-L301?qs=JUmsgfbaopRXkasA8RUqKg%3D%3D&countryCode=DE&currencyCode=EUR

#include "sensors.h"
#include "math.h"

volatile char adc_init = 0;

void adc_setup()
{
    /*--*/
    adc_init = 1;
}

/**
 * @param NTC specify here wich NTC y wanna check. dont specify anything or set to 255 checks the currently connected one
 * @return 1 if connected, 0 if not
 *  */
uint8_t temp_isconnected()
{
    if (temp_read_one() == -1000000.0)
    {
        return 0;
    }
    return 1;
}

/**
 * Reads out the temperature of one NTC thermistor.
 * Temperature range with current resistor values: 0.25 til 44.85°C
 * @return temperature value or -1000000 if NTC is not connected/vaulty
 */
float temp_read_one()
{
    /*circuit design*/
    const float VCC_NTC = 3.0;     // reference voltage for the NTC Readout
    const float R_SERIES = 5200.0; // Fixed resistor value in ohms (10kΩ)
    const float R41 = 10000.0;
    const float R43 = 51000.0;
    const float R53 = 10000.0;

    /*thermistor stats*/
    const float NTC_B = 3435.0;      // Beta parameter
    const float NTC_T0 = 298.15;         // Reference temperature in Kelvin (25°C)
    const float NTC_R0 = 10000.0;        // Resistance at reference temperature (10kΩ)

    /*calculations*/
    const float R43_paral_R41 = R41 * R43 / (R41 + R43);
    const float gain = 1.0 / (R43_paral_R41 / (R43_paral_R41 + R53));
    const float R41_paral_R41 = 0.5 * R41;
    const float voffset = VCC_NTC * R41_paral_R41 / (R41_paral_R41 + R43);

    if (!adc_init)
    {
        adc_setup();
    }

    /*Select ADC range to 2.048V*/

    /* check if NTC connected*/
    if (analogRead(PIN_TEMPADC) < ADC_MAX_READ * 0.05)
    {
        // error_handler(ERROR_NO_NTC_CONNECTED);
        return -1000000;
    }

    /*Read out ADC in a buffer and calculating adc_average*/
    int adc_buffer = 0;
     for (int i = 0; i < nTimes; i++)
    {
        adc_buffer += analogRead(ADC0);
    }
    float adc_average = ((float)adc_buffer) / nTimes;

    // /*removing spikes in adc_buffer*/
    // float voltage_adc;
    // unsigned int counter_spikes_removed = 0;
    // for (int i = 0; i < nTimes; i++)
    // {
    //     // debugf(">error:%f\n",adc_average-adc_buffer[i]);
    //     if (adc_buffer[i] > (adc_average + spike_tolerance) &&
    //         adc_buffer[i] < (adc_average - spike_tolerance))
    //     // replaces adc_buffer values which dividate from the adc_average about more than spike_tolerance
    //     {
    //         adc_buffer[i] = adc_average;
    //         counter_spikes_removed++;
    //     }
    // }
    // debugf("spikes removed:%u from %u samples\n", counter_spikes_removed, nTimes);

    // /*calculating new adc_average without spikes*/
    // float filtered_adc_average = 0;
    // for (int i = 0; i < nTimes; i++)
    // {
    //     filtered_adc_average += adc_buffer[i];
    // }
    // filtered_adc_average = filtered_adc_average / nTimes;

    /*calculating volgae form adc value*/
    float voltage_adc = (adc_average / ADC_MAX_READ) * VCC_NTC;

    /*Converts the adc voltage after the opamp circuit to the voltage on the ntc*/
    float volt_ntc = voltage_adc * (1.0 / gain) + voffset;

    /*Converts ADC value to a Resistance*/
    float resistance = (float)R_SERIES * (((float)VCC_NTC / volt_ntc) - 1);

    /*Calculate the temperature in Kelvin using the Steinhart–Hart equation*/
    float tempK = 1.0 / (1.0 / NTC_T0 + (1.0 / NTC_B) * log(resistance / NTC_R0));

    /*Convert temperature from Kelvin to Celsius*/
    float tempC = tempK - 273.15;
    // debugf_info("VADC:%f VNTC:%f R:%f T:%f\n", voltage_adc, volt_ntc, resistance, tempC);
    return tempC;
}

float ph_read(const float Temp_C){
    const float offset = 1.024;
    const float Faraday = 9.6485309*10000; //Faraday Constant
    const float R_const =  8.314510; //universal gas constan
    const float ln10 = 2.30258509299;//ln(10)
    float Temp_K = Temp_C + 273.15;

    /*Select ADC range to 2.048V*/

    float volt_meas = analogRead(ADC1);

    float ph = 7.0 + (volt_meas-offset) *  Faraday /(R_const*Temp_K*ln10);
    return ph;
}

float tia_read(){
    const float gain = 10*1000*1000;

    /*Select ADC range to 0.256V*/

    float volt_meas = analogRead(ADC2);
    float I_pd=volt_meas/gain;
    return I_pd;
}

float update_cur_integrator(){
    const float CAP_0 = 100; //nF
    const float CAP_1 = 10; //nF

    static last_volt_meas = analogRead(ADC3);
    static last_timestamp = micros();

    /*Select ADC range to 4.096V*/
    float volt_meas = analogRead(ADC3);
    float timestamp = micros();

    /*i_pd calculation over 2 samples*/
    float delta_v = last_volt_meas - volt_meas;
    float delta_t = timestamp-last_timestamp;
    float i_photodiode=C*delta_v/delta_t;

    /*i_pd calculation over complete discharge*/

    return i_photodiode;
}

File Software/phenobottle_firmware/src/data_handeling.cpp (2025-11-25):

#include "data_handeling.h"
#include "ADC_ADS1115.h"
#include "ArduinoJson.h"
#include "HWCDC.h"
#include "esp32-hal.h"
#include "imu.h"
#include "opt.h"
#include "pins.h"
#include "util.h"
#include <Arduino.h>

#define ANALOG_WRITE_RES 255
#define PERCENTAGE_TO_DUTY_CYCLE(p) /* fixed point percentage (0-100) to 8-bit duty cycle (0-255) */ \
  (p <= 0 ? 0 : p >= 100 ? ANALOG_WRITE_RES                                                          \
                         : (int)(p * ANALOG_WRITE_RES / 100))

/**
 * Checks for Commands send to the console
 * Is non-blocking and ment to be called frequently
 * * */
void Console::checkForInput()
{
  if (stream->available())
  {
    this->handleInput();
  }
}

void Console::printCommandPrompt()
{
  // print a simple prompt to show the user that the console is ready for input
  stream->print("> ");
  stream->flush();
}

/*Decodes and executes Commands send to console*/
void Console::handleInput()
{
  String buffer = stream->readStringUntil('\n');
  // stream->printf("Received data: %s\n", UserRxBufferFS);

  /*decode message*/
  char command[4] = {0}; // Store the command (e.g., "/C")
  float param0 = -1, param1 = -1, param2 = -1,
        param3 = -1; // Up to 4 parameters

  /*Use sscanf to extract the command and up to 4 floats*/
  int num_params = sscanf(buffer.c_str(), "%s %f %f %f %f", command, &param0,
                          &param1, &param2, &param3);

  // Print the command and the parameters
  /* stream->printf("~rec:%s|%f|%f|%f|%f|\n", command, param0, param1, param2,
   * param3);*/

  // encodes 4 char in one int to be compared by switch case
  int com_encoded = (int)((command[0] << 24) | (command[1] << 16) |
                          (command[2] << 8) | command[3]);

  switch (com_encoded)
  {
    /**here are the executions of all the commands */
    // case (int)('d' << 24 | 'f' << 16 | 'u' << 8 | 0): {
  /*help*/
  case (int)('?' << 24 | 0):
  {
    stream->print("\e[33m\n<help console>\n\e[0m");
    stream->print("structure of commands:\n");
    stream->print(
        "[str command][whitespace][param0=-1][whitespace][param1=-1]..\n");
    stream->print("examples:\n");
    stream->print("\"m 1 0.1 \":Set Motor 1 to 0.1(aka 10 percent\n");
    stream->print("\"p -1 1 -1 1000\":Print TIA every 1000ms\n");
    stream->print("command list:\n");
    stream->print("-?|this help screen\n");
    stream->print("-m|[number][duty_%][freq=100k]:\n"
                  "  sets motor [number] at"
                  "  [duty_%] power and optional [freq]Hz.\n");
    stream->print("-p|[NTC/pH/oD=0][TIA=0][IMU=0][Delay_ms=500]:\n"
                  "  change sensor output.\n"
                  "  0 disables, 1 enables, -1 no-change for given\n"
                  "  output. [Delay_ms] is between two prints. Less prints\n"
                  "  increases the maximal frequency\n");
    stream->print("-a|[duty_%]: sets Ambient Led at duty_%\n");
    stream->print("-o|: measure optical density\n");
    stream->print("-h|: hammer hit, record data and swing hammer\n");
    stream->print("\n");
    break;
  }

  case ('o' << 24 | 0):
  {
    stream->print("\e[33m\n<measure optical density>\n\e[0m");
    stream->flush();
    measure_OD(); // blocking
    stream->print("\e[33m\n<finished measuring optical density>\n\e[0m");
    break;
  }

  case ('h' << 24 | 0):
  {
    stream->print("\e[33m\n<hammer hit>\n\e[0m");
    stream->flush();
    hammer_hit(); // blocking
    stream->print("\e[33m\n<finished hammer hit>\n\e[0m");
    break;
  }

    /*control recieving data stream*/
  case ('p' << 24 | 0):
  {
    if (param0 >= 0)
      config_print.NTC_PH_OD = (bool)param0;
    if (param1 >= 0)
      config_print.TIA = (bool)param1;
    if (param2 >= 0)
      config_print.IMU = (bool)param2;
    if (param3 >= 0)
      config_print.DELAY = (unsigned long)param3;

    config_print.OPT = true; // FIXME cannot control OPT prints, due to 4 parameter limit!

    break;
  }

    /*control motors*/
  case ('m' << 24 | 0):
  {
    analogWriteResolution(8);

    if (param2 > 1)
    {
      analogWriteFrequency(param2);
    }

    int duty = PERCENTAGE_TO_DUTY_CYCLE(param1);

    if ((int)param0 == 0)
    {
      stream->printf("set motor 0 to %i\n", duty);
      analogWrite(PIN_MOTOR0, duty);
      pwm_config.motor0_duty = duty;
    }
    if ((int)param0 == 1)
    {
      stream->printf("set motor 1 to %i\n", duty);
      analogWrite(PIN_MOTOR1, duty);
      pwm_config.motor1_duty = duty;
    }
    if ((int)param0 == 2)
    {
      stream->printf("set motor 2 to %i\n", duty);
      analogWrite(PIN_MOTOR2, duty);
      pwm_config.motor2_duty = duty;
    }
    break;
  }

    /*control ambient light*/
  case ('a' << 24 | 0):
  {
    analogWriteResolution(8);

    int duty = PERCENTAGE_TO_DUTY_CYCLE(param0);

    if ((int)param0 >= 0)
    {
      stream->printf("set ambient led to %i\n", duty);
      analogWrite(PIN_AMBIENT_LED, duty);
      pwm_config.ambient_led_duty = duty;
    }
    break;
  }

  default:
  {
    stream->printf("unknown commnad: %s\n", command);
    stream->print("use \"?\" for help\n");
    break;
  }
  }

  printCommandPrompt();
}

/**
 * Sends Sensor data specified by struct sendSensorDataConfig .
 * Is non-blocking and ment to be called frequently
 * */
void Console::sendSensorData() const
{
  static unsigned long timestamp = millis() + config_print.DELAY;

  if (millis() > timestamp)
  {
    timestamp = millis() + config_print.DELAY;

    // unsigned long timestamp_o = micros(); // for transimmion timing

    /*Output format*/
    JsonDocument doc;
    if (config_print.NTC_PH_OD | config_print.IMU | config_print.TIA)
    {
      doc["time"] = millis();
    }

    /*ADC*/
    if (config_print.NTC_PH_OD)
    {
      doc["NTC"] = readNTC();
      doc["pH_cal"] = readPH(readNTC());
      const float TEMPERATURE_ROOM = 25.0;
      doc["pH"] = readPH(TEMPERATURE_ROOM);
    }

    if (config_print.TIA)
    {
      doc["TIA"] = readTIA();
    }

    /*IMU*/
    if (config_print.IMU)
    {
      if (init_imu)
      {
        inv_imu_sensor_event_t imu_event;
        // Get last event
        IMU.getDataFromRegisters(imu_event);
        doc["imu"]["a"][0] = imu_event.accel[0];
        doc["imu"]["a"][1] = imu_event.accel[1];
        doc["imu"]["a"][2] = imu_event.accel[2];
        doc["imu"]["g"][0] = imu_event.gyro[0];
        doc["imu"]["g"][1] = imu_event.gyro[1];
        doc["imu"]["g"][2] = imu_event.gyro[2];
        doc["imu"]["t"] = imu_event.temperature;
      }
    }

    if (config_print.OPT)
    {
      // libarary name "lux" is wrong, should be "irradiance"
      if (!opt3002_left_queue.empty())
      {
        OPT3002 result = opt3002_left_queue.front();
        opt3002_left_queue.pop();
        doc["opt"]["left"] = result.lux;
      }

      if (!opt3002_right_queue.empty())
      {
        OPT3002 result = opt3002_right_queue.front();
        opt3002_right_queue.pop();
        doc["opt"]["right"] = result.lux;
      }
    }

    /*Send Data*/
    if (!doc.isNull())
    {
      serializeJson(doc, *stream);
      // serializeJsonPretty
      stream->print("\n");
    }

    /*Time Transmission*/
    // long int timestamp_a = micros();
    // stream->printf("t:%ims\n", (timestamp_a - timestamp_o) / 1000.0);
  }
}

/**
 * Toggle every DELAY_MS Seconds.
 */
void Console::toggle_status_led()
{
  const unsigned long DELAY_MS = 500;
  static char status = 2;
  static unsigned long timestamp = millis() + DELAY_MS;

  // setup condition
  if (status == 2)
  {
    pinMode(PIN_LED_STATUS, OUTPUT);
    status = 0;
  }

  // toggle LED
  if (millis() > timestamp)
  {
    timestamp = millis() + DELAY_MS;
    status = !status;
    digitalWrite(PIN_LED_STATUS, status);
  }
}
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
